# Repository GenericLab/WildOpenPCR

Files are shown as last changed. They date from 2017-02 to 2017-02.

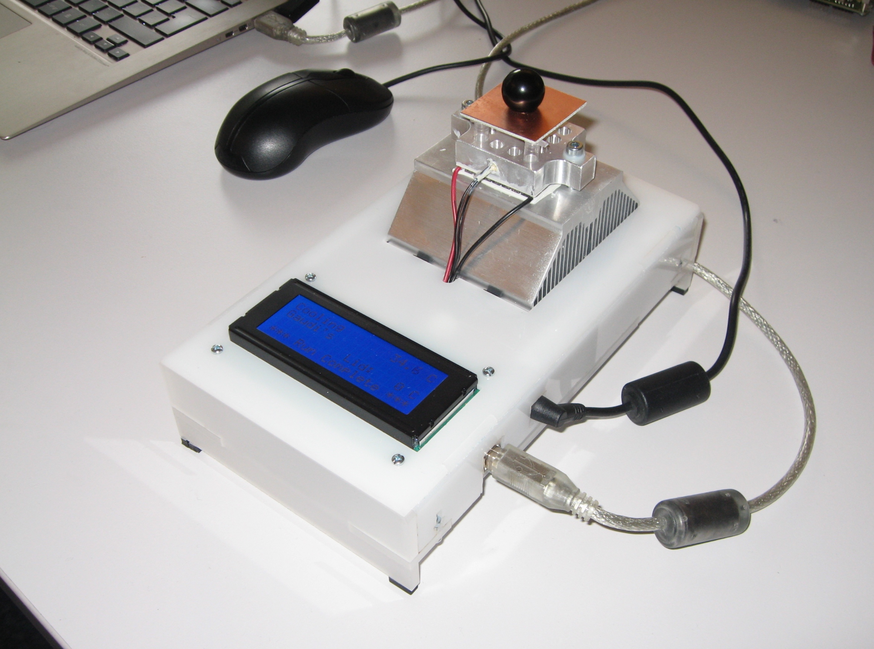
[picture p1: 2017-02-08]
Images/WildOpenPCR.JPG

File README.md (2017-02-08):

# WildOpenPCR
DIY derivate of the OpenPCR Project.
Original design of OpenPCR by Tito Jakowski and Jeff Perfutto: http://openpcr.org/

For more info see: http://wlu18www30.webland.ch/wiki/Wild_OpenPCR

and: http://www.gaudi.ch/GaudiLabs/?page_id=328

All OpenPCR software, design files and instructions are licensed under the GNU GPLv3.

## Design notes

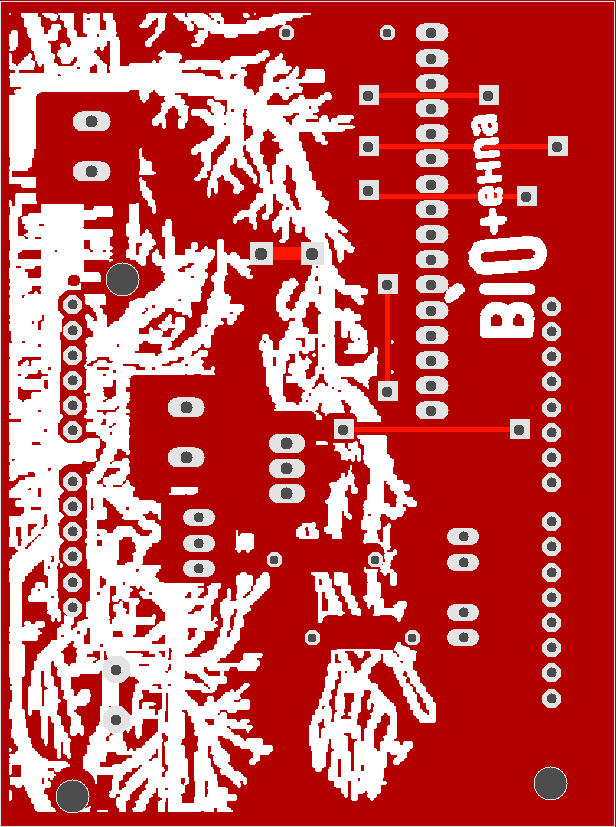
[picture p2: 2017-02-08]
Images/PCRBottom.png

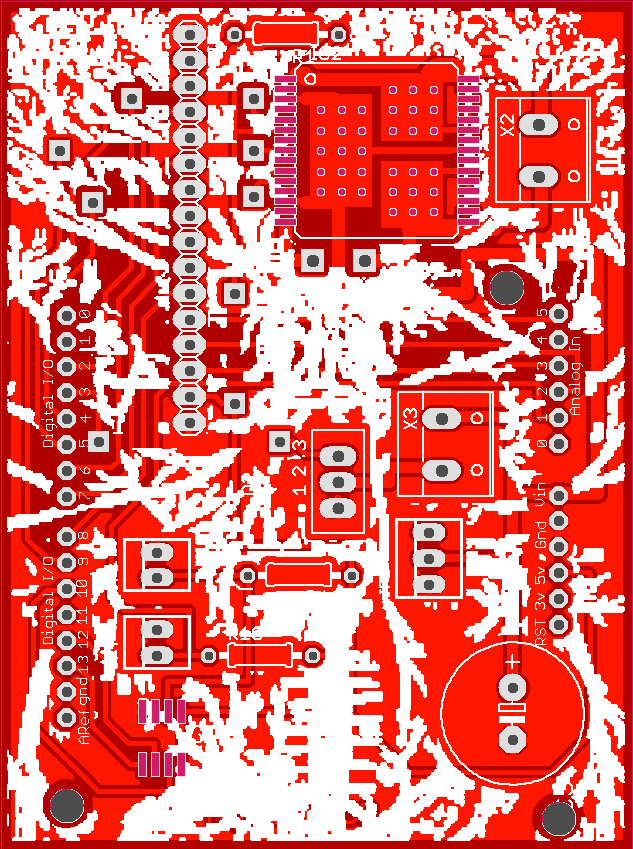
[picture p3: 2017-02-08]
Images/PCRTop.png

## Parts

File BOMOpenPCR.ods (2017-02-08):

 | PART LIST / BILL OF MATERIAL
 | MyOpenPCR
 | Exported |  | from OpenPCRGaudi.b
 | Part | No | Description | Package | Library Position (inc | Price
x | C3 | 1 | 1000 uF, 25V, 5.08 mm RAD 470/35 | E5-13 | rcl (1.975 0.525) |  |  | 5 | 2x 470
x | IC1 | 1 | MCP 3551-E/SN :: A/D Converter / 18-bit / 1-Kanal / 4sps / SO-8 | SO-08 | microchip (0.62 0.43) | 3.7 | 3.7 | 5 | 2
x | IC2 | 1 | VNH 3SP30 :: H-Bridge Motor Driver 30A Power, MSOP-30 | MULTIPOWERSO-30 | Gaudi (1.45 2.7) | 5.5 | 5.5 | 5 | 2
x | JP1 | 1 | 1X16 pinheader MPE 094-1-016 / BL 1X20W 2,54 |  | pinhead (0.725 2.4) |  |  | 5
x | JP2 | 1 | 1x3 pinheader / connector (2.54 mm) SL 1X36G 2,54 | 22-23-2031 | con-molex (1.65 1.125)
x | JP3 | 1 | 1x2 pinheader / connector (2.54 mm) | 22-23-2021 | con-molex (0.6 1.1)
x | JP4 | 1 | 1x2 pinheader / connector (2.54 mm) | 22-23-2021 | con-molex (0.6 0.8)
x | Q2 | 1 | BSS97 / IRFI 540N | TO202 | openpcr (1.1 1.42) | 0.8 | 0.8 | 5 | 2
x | R1 | 1 | 68 Ohm / 1W 68 | 0207/10 | resistor (1.1 3.15) |  |  | 10 | 6
x | R4 | 1 | 2.2 kOhm / METALL 2,20K | 0207/10 | resistor (1.15 1.06) |  |  | 20 | 10
x | R10 | 1 | 2.2 kOhm / METALL 2,20K | 0207/10 | resistor (1 0.75)
 | U$3 | 1 | ARDUINO UNO :: Arduino Uno Rev. 3, ATmega328, USB | ARDUINO | openpcr (2.25 -0.45) | 18.5 | 18.5 | 3 |  | ricardo
x | X2 | 1 | RND 205-00232 1x2 Connetor (5.08 mm) | W237-132 | con-wago-508 (2.1 2.7) |  |  | 10 | 4
x | X3 | 1 | RND 205-00232 1x2 Connetor (5.08 mm) | W237-132 | con-wago-508 (1.725 1.565)
x | NTC | 2 | HYG NTC 103 :: Präzisions-Temperatursensor TS-NTC-103 |  |  | 2.2 | 4.4 | 5 | 3x 1x ohne A
x | LCD | 1 | LCD 204B BL :: LCD Dot-Matrix-Modul, 4x20 Zeichen, blau |  |  | 20 | 20 | 3 | 1
x | PELTIER | 1 | TECB 1 :: Thermo-Modul, Peltierelement, 40x40x3,8mm | 51.4W |  | 19.4 | 19.4 | 3 | 2
 | PELTIER |  | TECB 3 :: Thermo-Modul, Peltierelement, 40x40x3,3mm | 68.6W |  |  |  | 3 | 2
x | MyOpenPCR_PCB
x | TOP_HEATER PCB |  | LidHeater.brd
x | PCB Cooler
 | HEAT_BLOCK
x | POWER SUPPLY | 1 | MW GST90A12 :: Tischnetzteil 80 W, 12 V / 6,67 A |  |  | 28.6 | 28.6
 | Cables (Flat) Jumper |  |  |  |  |  |  |  |  | Ricardo /
 |  |  |  |  |  |  | 100.9
 | PCB Corrections |  | Dickere Brücken
 |  |  | Pin Durchmesser Chechen
 |  |  | Power Anschluss (Pads +/-)
 | Laser: |  | IRLR 120N

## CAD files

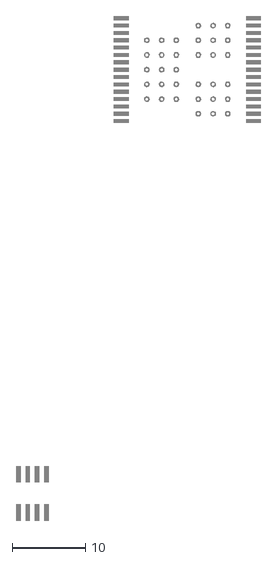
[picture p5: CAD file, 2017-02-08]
MyOpenPCR/OpenPCRGaudi.dxf
33.3 x 68.6

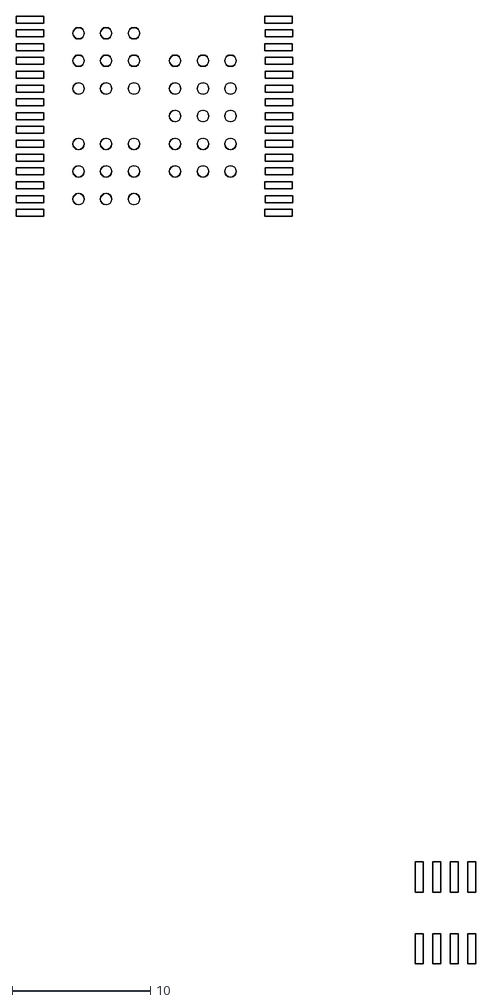
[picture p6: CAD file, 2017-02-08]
Stencils/OpenPCR_Stencil.dxf
33.3 x 68.6

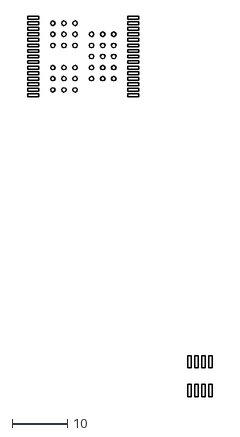
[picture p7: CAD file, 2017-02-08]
Stencils/OpenPCR_Stencil2.dxf
33.3 x 68.6

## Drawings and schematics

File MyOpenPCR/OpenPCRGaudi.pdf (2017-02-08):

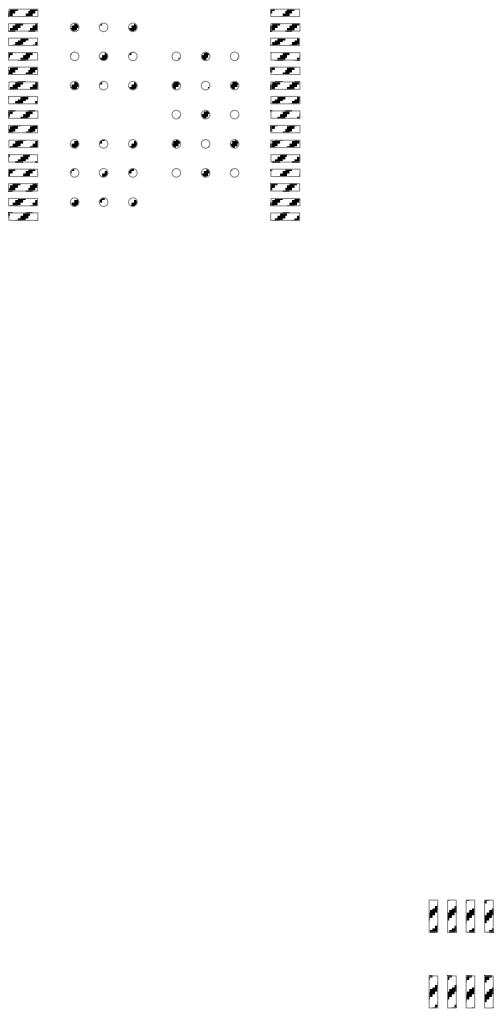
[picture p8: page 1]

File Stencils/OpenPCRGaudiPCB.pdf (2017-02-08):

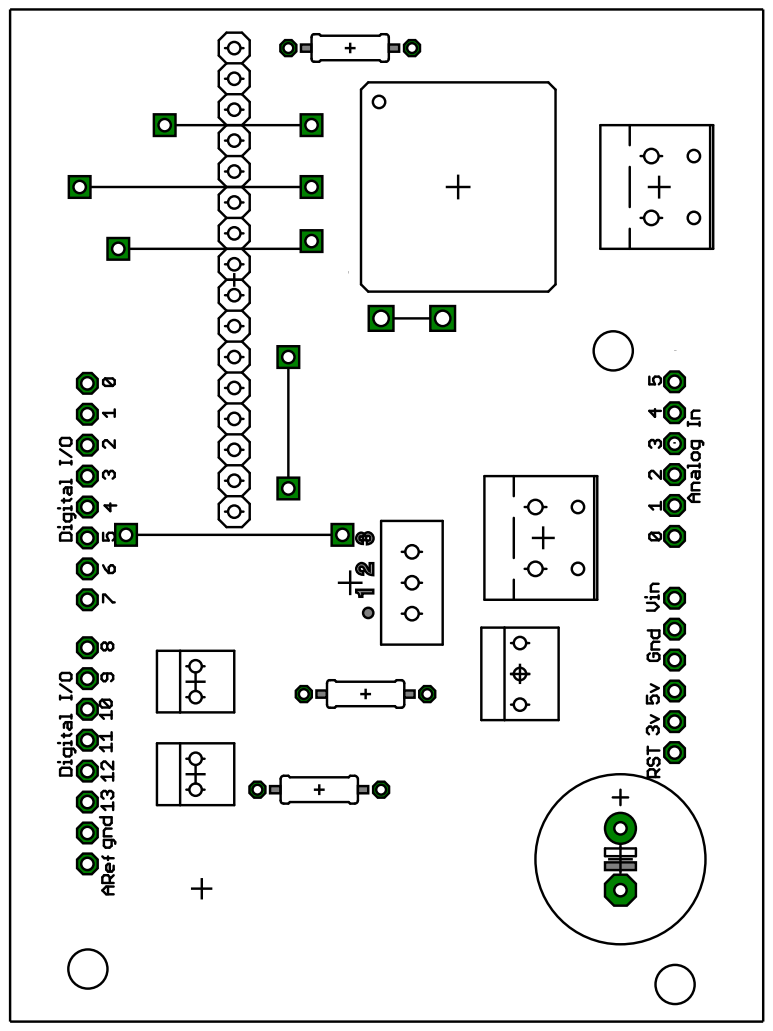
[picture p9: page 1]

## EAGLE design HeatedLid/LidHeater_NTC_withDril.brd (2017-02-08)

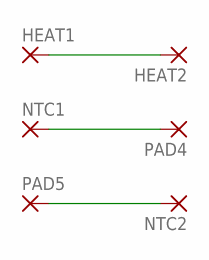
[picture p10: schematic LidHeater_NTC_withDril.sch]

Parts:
HEAT1, HEAT2: SMD5; SMD2,54-5,08
NTC1, NTC2: SMD5; SMD2,54-5,08
PAD4, PAD5: SMD5; SMD2,54-5,08

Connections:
unnamed: HEAT1.1, HEAT2.1
unnamed: NTC1.1, PAD4.1
unnamed: NTC2.1, PAD5.1

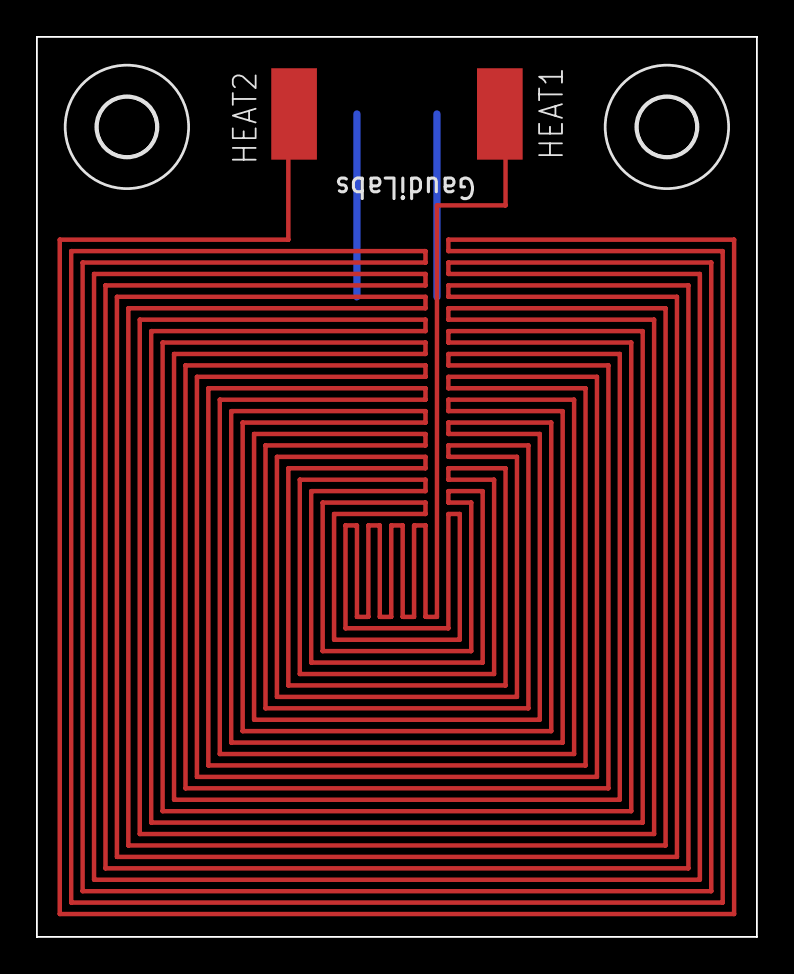
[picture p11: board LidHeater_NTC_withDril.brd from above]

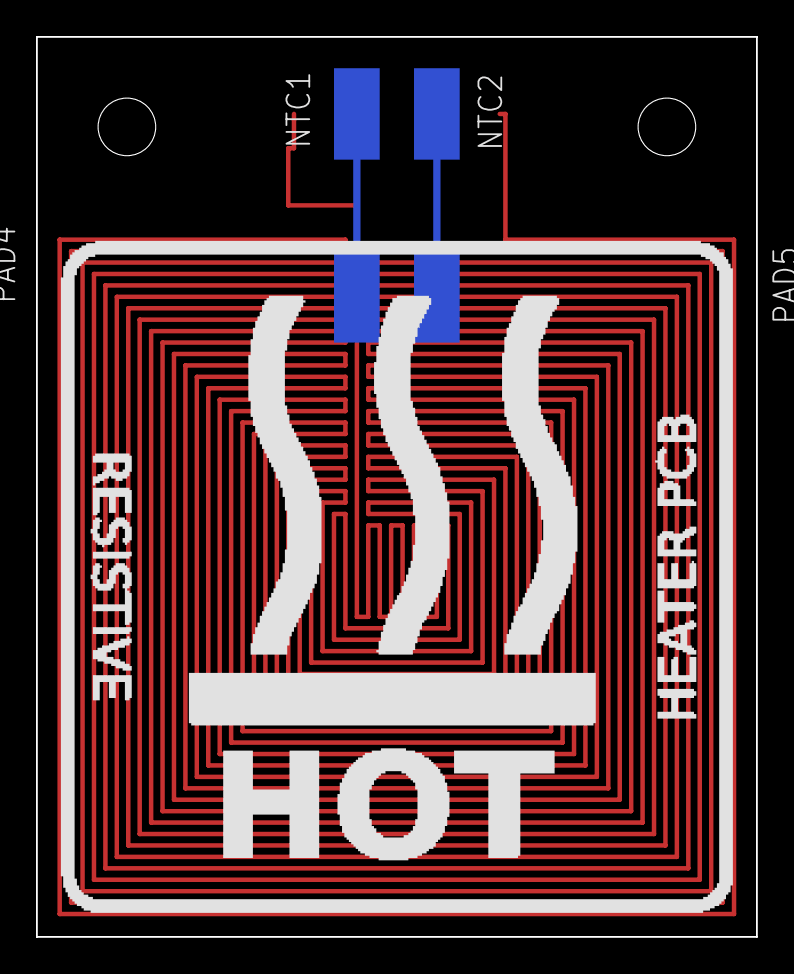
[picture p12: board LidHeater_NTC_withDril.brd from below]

Board: 2 copper layers, 40.0 x 50.0 mm, 8 parts (4 on the bottom side), 3 nets.

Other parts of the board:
U$1, U$2: 3,2

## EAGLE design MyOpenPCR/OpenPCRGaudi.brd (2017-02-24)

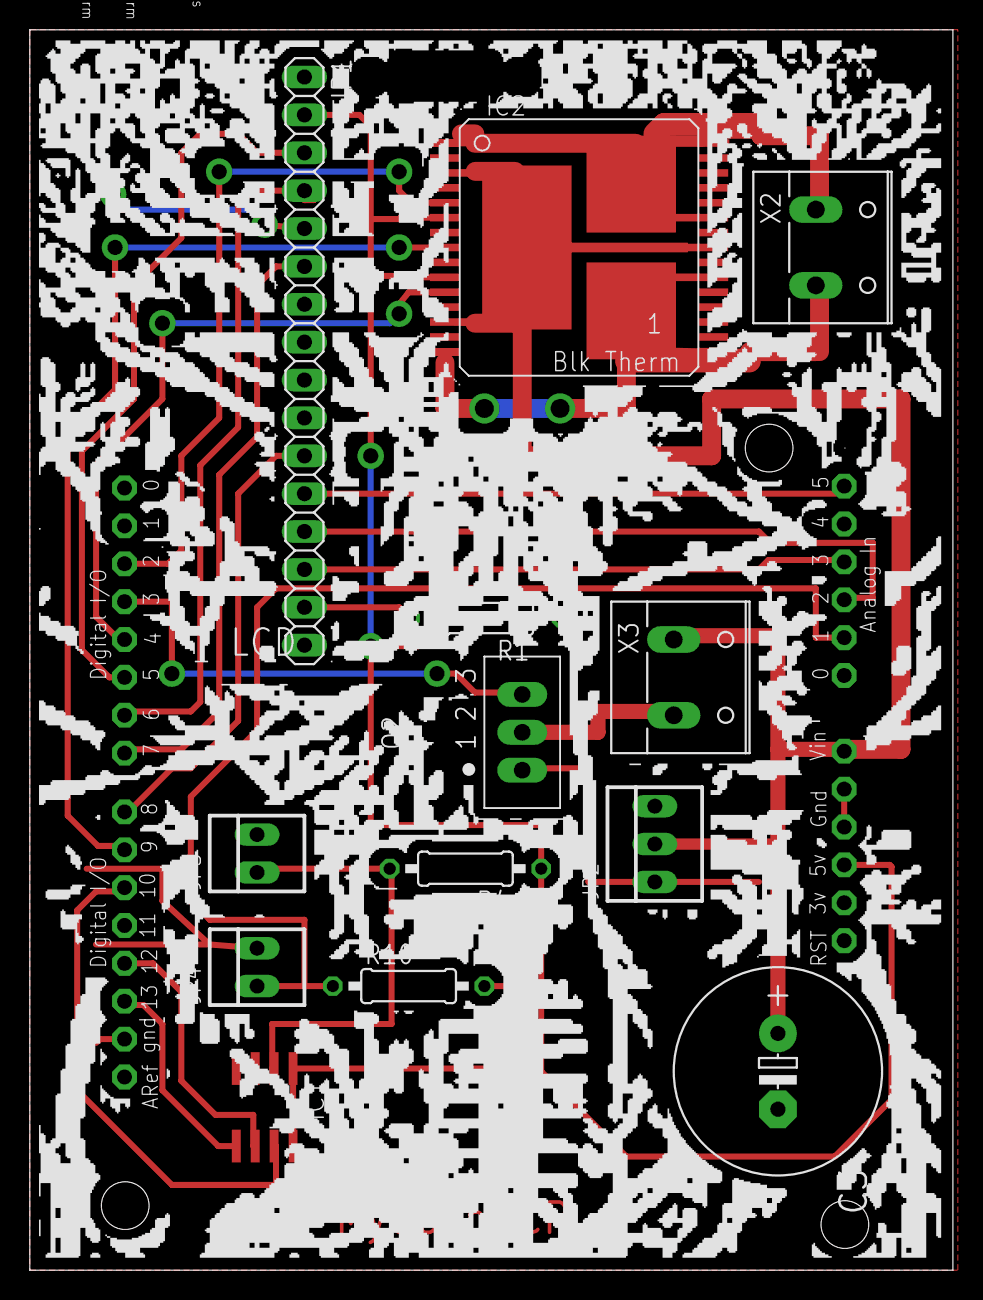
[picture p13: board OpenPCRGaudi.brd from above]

Board: 2 copper layers, 61.9 x 83.2 mm, 14 parts (0 on the bottom side), 23 nets.

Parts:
C3: E5-13
IC1: MCP3551SN; SO-08
IC2: VNH3SP30_2; MULTIPOWERSO-30
JP1: 1X16
JP2: 22-23-2031
JP3, JP4: 22-23-2021
Q2: BSS97; TO202
R1, R4, R10: 0207/10
U$3: ARDUINODUEMILANOVE; ARDUINO
X2, X3: W237-132

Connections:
+5VREG: IC1.1, IC1.8, IC2.6, IC2.10, JP1.2, R1.1, R4.1, R10.2, U$3.5V
+12V1: C3.+, IC2.3, IC2.13, IC2.23, IC2.VCC, IC2.VCC@1, JP2.2, U$3.VIN, X3.1
GND1: C3.-, IC1.3, IC1.4, IC2.18, IC2.19, IC2.20, IC2.26, IC2.27, IC2.28, JP1.1, JP1.5, JP1.16, JP2.1, JP3.2, JP4.2, Q2.1, U$3.GND, U$3.GND1, U$3.GND2
unnamed: JP1.3, U$3.D5
unnamed: JP1.4, U$3.D6
unnamed: JP1.14, U$3.A3
unnamed: JP1.15, R1.2
unnamed: Q2.3, U$3.D3
unnamed: JP1.13, U$3.A2
unnamed: JP1.6, U$3.D7
unnamed: JP1.12, U$3.A5
unnamed: IC1.5, U$3.D13
unnamed: Q2.2, X3.2
unnamed: JP1.11, U$3.D8
unnamed: IC1.2, JP3.1, R4.2
unnamed: IC2.1, IC2.25, IC2.30, IC2.GND, IC2.OUTA, X2.1
unnamed: IC1.6, U$3.D12
unnamed: IC1.7, U$3.D10
unnamed: IC2.8, U$3.D9
unnamed: IC2.11, U$3.D4
unnamed: IC2.15, IC2.16, IC2.21, IC2.OUTB, IC2.SS, X2.2
unnamed: IC2.5, U$3.D2
unnamed: JP4.1, R10.1, U$3.A1

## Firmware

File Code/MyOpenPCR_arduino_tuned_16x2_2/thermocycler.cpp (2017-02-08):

/*
 *  thermocycler.cpp - OpenPCR control software.
 *  Copyright (C) 2010-2012 Josh Perfetto. All Rights Reserved.
 *
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
 *  You should have received a copy of the GNU General Public License along with
 *  the OpenPCR control software.  If not, see <http://www.gnu.org/licenses/>.
 */

#include "pcr_includes.h"
#include "thermocycler.h"

#include "display.h"
#include "program.h"
#include "serialcontrol.h"
#include "../Wire/Wire.h"
#include <avr/pgmspace.h>

//constants
  
// I2C address for MCP3422 - base address for MCP3424
#define MCP3422_ADDRESS 0X68
#define MCP342X_RES_FIELD  0X0C // resolution/rate field
#define MCP342X_18_BIT     0X0C // 18-bit 3.75 SPS
#define MCP342X_BUSY       0X80 // read: output not ready

#define CYCLE_START_TOLERANCE 0.2
#define LID_START_TOLERANCE 1.0

#define PLATE_PID_INC_NORM_P 3000
#define PLATE_PID_INC_NORM_I 750
#define PLATE_PID_INC_NORM_D 3000

#define PLATE_PID_INC_LOW_THRESHOLD 40
#define PLATE_PID_INC_LOW_P 600
#define PLATE_PID_INC_LOW_I 200
#define PLATE_PID_INC_LOW_D 400

#define PLATE_PID_DEC_HIGH_THRESHOLD 70
#define PLATE_PID_DEC_HIGH_P 800
#define PLATE_PID_DEC_HIGH_I 700
#define PLATE_PID_DEC_HIGH_D 300

#define PLATE_PID_DEC_NORM_P 3000
#define PLATE_PID_DEC_NORM_I 750
#define PLATE_PID_DEC_NORM_D 3000

#define PLATE_PID_DEC_LOW_THRESHOLD 35
#define PLATE_PID_DEC_LOW_P 2000
#define PLATE_PID_DEC_LOW_I 100
#define PLATE_PID_DEC_LOW_D 200

#define PLATE_BANGBANG_THRESHOLD 2.0

#define MIN_PELTIER_PWM -1023
#define MAX_PELTIER_PWM 1023

#define MAX_LID_PWM 255
#define MIN_LID_PWM 0

#define STARTUP_DELAY 4000

//pid parameters
const SPIDTuning LID_PID_GAIN_SCHEDULE[] = {
  //maxTemp, kP, kI, kD
  { 70, 40, 0.15, 60 },
  { 200, 80, 1.1, 10 }
};

//public
Thermocycler::Thermocycler(boolean restarted):
  iRestarted(restarted),
  ipDisplay(NULL),
  ipProgram(NULL),
  ipDisplayCycle(NULL),
  ipSerialControl(NULL),
  iProgramState(EStartup),
  ipPreviousStep(NULL),
  ipCurrentStep(NULL),
  iThermalDirection(OFF),
  iPeltierPwm(0),
  iCycleStartTime(0),
  iRamping(true),
  iPlatePid(&iPlateThermistor.GetTemp(), &iPeltierPwm, &iTargetPlateTemp, PLATE_PID_INC_NORM_P, PLATE_PID_INC_NORM_I, PLATE_PID_INC_NORM_D, DIRECT),
  iLidPid(LID_PID_GAIN_SCHEDULE, MIN_LID_PWM, MAX_LID_PWM),
  iTargetLidTemp(0) {
    
  ipDisplay = new Display();
  ipSerialControl = new SerialControl(ipDisplay);
  
  //init pins
  pinMode(15, INPUT);
  pinMode(2, OUTPUT);
  pinMode(3, OUTPUT);
  pinMode(4, OUTPUT);
  pinMode(5, OUTPUT);
  
    // SPCR = 01010000
  //interrupt disabled,spi enabled,msb 1st,master,clk low when idle,
  //sample on leading edge of clk,system clock/4 rate (fastest)
  int clr;
  SPCR = (1<<SPE)|(1<<MSTR)|(1<<4);
  clr=SPSR;
  clr=SPDR;
  delay(10); 

  iPlatePid.SetOutputLimits(MIN_PELTIER_PWM, MAX_PELTIER_PWM);
  
  // Peltier PWM
  TCCR1A |= (1<<WGM11) | (1<<WGM10);
  TCCR1B = _BV(CS21);
  
  // Lid PWM
  TCCR2A = _BV(COM2A1) | _BV(COM2B1) | _BV(WGM21) | _BV(WGM20);
  TCCR2B = _BV(CS22);

  iszProgName[0] = '\0';
}

Thermocycler::~Thermocycler() {
  delete ipSerialControl;
  delete ipDisplay;
}

// accessors
int Thermocycler::GetNumCycles() {
  return ipDisplayCycle->GetNumCycles();
}

int Thermocycler::GetCurrentCycleNum() {
  int numCycles = GetNumCycles();
  return ipDisplayCycle->GetCurrentCycle() > numCycles ? numCycles : ipDisplayCycle->GetCurrentCycle();
}

Thermocycler::ThermalState Thermocycler::GetThermalState() {
  if (iProgramState == EStartup || iProgramState == EStopped)
    return EIdle;
  
  if (iRamping) {
    if (ipPreviousStep != NULL) {
      return ipCurrentStep->GetTemp() > ipPreviousStep->GetTemp() ? EHeating : ECooling;
    } else {
      return iThermalDirection == HEAT ? EHeating : ECooling;
    }
  } else {
    return EHolding;
  }
}
 
// control
void Thermocycler::SetProgram(Cycle* pProgram, Cycle* pDisplayCycle, const char* szProgName, int lidTemp) {
  Stop();

  ipProgram = pProgram;
  ipDisplayCycle = pDisplayCycle;

  strcpy(iszProgName, szProgName);
  iTargetLidTemp = lidTemp;
}

void Thermocycler::Stop() {
  iProgramState = EStopped;
  
  ipProgram = NULL;
  ipPreviousStep = NULL;
  ipCurrentStep = NULL;
  
  iStepPool.ResetPool();
  iCyclePool.ResetPool();
  
  ipDisplay->Clear();
}

PcrStatus Thermocycler::Start() {
  if (ipProgram == NULL)
    return ENoProgram;
  
  //advance to lid wait state
  iProgramState = ELidWait;
  
  return ESuccess;
}
    
// internal
void Thermocycler::Loop() {
  switch (iProgramState) {
  case EStartup:
    if (millis() > STARTUP_DELAY) {
      iProgramState = EStopped;
      
      if (!iRestarted && !ipSerialControl->CommandReceived()) {
        //check for stored program
        SCommand command;
        if (ProgramStore::RetrieveProgram(command, (char*)ipSerialControl->GetBuffer()))
          ProcessCommand(command);
      }
    }
    break;

  case ELidWait:    
    if (GetLidTemp() >= iTargetLidTemp - LID_START_TOLERANCE) {
      //lid has warmed, begin program
      iThermalDirection = OFF;
      iPeltierPwm = 0;
      PreprocessProgram();
      iProgramState = ERunning;
      
      ipProgram->BeginIteration();
      AdvanceToNextStep();
      
      iProgramStartTimeMs = millis();
    }
    break;
  
  case ERunning:
    //update program
    if (iProgramState == ERunning) {
      if (iRamping && abs(ipCurrentStep->GetTemp() - GetPlateTemp()) <= CYCLE_START_TOLERANCE && GetRampElapsedTimeMs() > ipCurrentStep->GetRampDurationS() * 1000) {
        //begin step hold
        
        //eta updates
        if (ipCurrentStep->GetRampDurationS() == 0) {
          //fast ramp
          iElapsedFastRampDegrees += absf(GetPlateTemp() - iRampStartTemp);
          iTotalElapsedFastRampDurationMs += millis() - iRampStartTime;
        }
        
        if (iRampStartTemp > GetPlateTemp())
          iHasCooled = true;
        iRamping = false;
        iCycleStartTime = millis();
        
      } else if (!iRamping && !ipCurrentStep->IsFinal() && millis() - iCycleStartTime > (unsigned long)ipCurrentStep->GetStepDurationS() * 1000) {
        //begin next step
        AdvanceToNextStep();
          
        //check for program completion
        if (ipCurrentStep == NULL || ipCurrentStep->IsFinal())
          iProgramState = EComplete;        
      }
    }
    break;
    
  case EComplete:
    if (iRamping && ipCurrentStep != NULL && abs(ipCurrentStep->GetTemp() - GetPlateTemp()) <= CYCLE_START_TOLERANCE)
      iRamping = false;
    break;
  }
  
  //lid 
  iLidThermistor.ReadTemp();
  ControlLid();
  
  //plate  
  iPlateThermistor.ReadTemp();
  CalcPlateTarget();
  ControlPeltier();
  
  //program
  UpdateEta();
  ipDisplay->Update();
  ipSerialControl->Process();
}

//private
void Thermocycler::AdvanceToNextStep() {
  ipPreviousStep = ipCurrentStep;
  ipCurrentStep = ipProgram->GetNextStep();
  if (ipCurrentStep == NULL)
    return;
  
  //update eta calc params
  if (ipPreviousStep == NULL || ipPreviousStep->GetTemp() != ipCurrentStep->GetTemp()) {
    iRamping = true;
    iRampStartTime = millis();
    iRampStartTemp = GetPlateTemp();
  } else {
    iCycleStartTime = millis(); //next step starts immediately
  }
  
  CalcPlateTarget();
  SetPlateControlStrategy();
}

void Thermocycler::SetPlateControlStrategy() {
  if (InControlledRamp())
    return;
    
  if (absf(iTargetPlateTemp - GetPlateTemp()) >= PLATE_BANGBANG_THRESHOLD && !InControlledRamp()) {
    iPlateControlMode = EBangBang;
    iPlatePid.SetMode(MANUAL);
  } else {
    iPlateControlMode = EPIDPlate;
    iPlatePid.SetMode(AUTOMATIC);
  }
  
  if (iRamping) {
    if (iTargetPlateTemp >= GetPlateTemp()) {
      iDecreasing = false;
      if (iTargetPlateTemp < PLATE_PID_INC_LOW_THRESHOLD)
        iPlatePid.SetTunings(PLATE_PID_INC_LOW_P, PLATE_PID_INC_LOW_I, PLATE_PID_INC_LOW_D);
      else
        iPlatePid.SetTunings(PLATE_PID_INC_NORM_P, PLATE_PID_INC_NORM_I, PLATE_PID_INC_NORM_D);

    } else {
      iDecreasing = true;
      if (iTargetPlateTemp > PLATE_PID_DEC_HIGH_THRESHOLD)
        iPlatePid.SetTunings(PLATE_PID_DEC_HIGH_P, PLATE_PID_DEC_HIGH_I, PLATE_PID_DEC_HIGH_D);
      else if (iTargetPlateTemp < PLATE_PID_DEC_LOW_THRESHOLD)
        iPlatePid.SetTunings(PLATE_PID_DEC_LOW_P, PLATE_PID_DEC_LOW_I, PLATE_PID_DEC_LOW_D);
      else
        iPlatePid.SetTunings(PLATE_PID_DEC_NORM_P, PLATE_PID_DEC_NORM_I, PLATE_PID_DEC_NORM_D);
    }
  }
}

void Thermocycler::CalcPlateTarget() {
  if (ipCurrentStep == NULL)
    return;
  
  if (InControlledRamp()) {
    //controlled ramp
    double tempDelta = ipCurrentStep->GetTemp() - ipPreviousStep->GetTemp();
    double rampPoint = (double)GetRampElapsedTimeMs() / (ipCurrentStep->GetRampDurationS() * 1000);
    iTargetPlateTemp = ipPreviousStep->GetTemp() + tempDelta * rampPoint;
    
  } else {
    //fast ramp
    iTargetPlateTemp = ipCurrentStep->GetTemp();
  }
}

void Thermocycler::ControlPeltier() {
  ThermalDirection newDirection = OFF;
  
  if (iProgramState == ERunning || (iProgramState == EComplete && ipCurrentStep != NULL)) {
    // Check whether we are nearing target and should switch to PID control
    if (iPlateControlMode == EBangBang && absf(iTargetPlateTemp - GetPlateTemp()) < PLATE_BANGBANG_THRESHOLD) {
      iPlateControlMode = EPIDPlate;
      iPlatePid.SetMode(AUTOMATIC);
      iPlatePid.ResetI();
    }
 
    // Apply control mode
    if (iPlateControlMode == EBangBang)
      iPeltierPwm = iTargetPlateTemp > GetPlateTemp() ? MAX_PELTIER_PWM : MIN_PELTIER_PWM;
    iPlatePid.Compute();
    
    if (iDecreasing && iTargetPlateTemp > PLATE_PID_DEC_LOW_THRESHOLD) {
      if (iTargetPlateTemp < GetPlateTemp())
        iPlatePid.ResetI();
      else
        iDecreasing = false;
    } 
    
    if (iPeltierPwm > 0)
      newDirection = HEAT;
    else if (iPeltierPwm < 0)
      newDirection = COOL; 
    else
      newDirection = OFF;
  } else {
    iPeltierPwm = 0;
  }
  
  iThermalDirection = newDirection;
  SetPeltier(newDirection, abs(iPeltierPwm));
}

void Thermocycler::ControlLid() {
  int drive = 0;  
  if (iProgramState == ERunning || iProgramState == ELidWait)
    drive = iLidPid.Compute(iTargetLidTemp, GetLidTemp());
 
  analogWrite(3, drive);
}

//PreprocessProgram initializes ETA parameters and validates/modifies ramp conditions
void Thermocycler::PreprocessProgram() {
  Step* pCurrentStep;
  Step* pPreviousStep = NULL;
  
  iProgramHoldDurationS = 0;
  iEstimatedTimeRemainingS = 0;
  iHasCooled = false;
  
  iProgramControlledRampDurationS = 0;
  iProgramFastRampDegrees = 0;
  iElapsedFastRampDegrees = 0;
  iTotalElapsedFastRampDurationMs = 0;  
  
  ipProgram->BeginIteration();
  while ((pCurrentStep = ipProgram->GetNextStep()) && !pCurrentStep->IsFinal()) {
    //validate ramp
    if (pPreviousStep != NULL && pCurrentStep->GetRampDurationS() * 1000 < absf(pCurrentStep->GetTemp() - pPreviousStep->GetTemp()) * PLATE_FAST_RAMP_THRESHOLD_MS) {
      //cannot ramp that fast, ignored set ramp
      pCurrentStep->SetRampDurationS(0);
    }
    
    //update eta hold
    iProgramHoldDurationS += pCurrentStep->GetStepDurationS();
 
    //update eta ramp
    if (pCurrentStep->GetRampDurationS() > 0) {
      //controlled ramp
      iProgramControlledRampDurationS += pCurrentStep->GetRampDurationS();
    } else {
      //fast ramp
      double previousTemp = pPreviousStep ? pPreviousStep->GetTemp() : GetPlateTemp();
      iProgramFastRampDegrees += absf(previousTemp - pCurrentStep->GetTemp()) - CYCLE_START_TOLERANCE;
    }
    
    pPreviousStep = pCurrentStep;
  }
}
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

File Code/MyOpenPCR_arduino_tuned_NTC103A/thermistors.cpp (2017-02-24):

/*
 *  program.cpp - OpenPCR control software.
 *  Copyright (C) 2010-2012 Josh Perfetto. All Rights Reserved.
 *
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
 *  You should have received a copy of the GNU General Public License along with
 *  the OpenPCR control software.  If not, see <http://www.gnu.org/licenses/>.
 */

#include "pcr_includes.h"
#include "thermistors.h"

// lid resistance table, in Ohms
PROGMEM const unsigned int LID_RESISTANCE_TABLE[] = {  
33890,32138,30487,28933,27468,26088,24785,23557,22397,21302,
20268,19291,18367,17493,16667,15885,15145,14444,13780,13151
12554,11988,11452,10942,10459,10000,9564,9150,8756,8382
8026,7687,7365,7058,6765,6487,6222,5969,5728,5499
5279,5070,4871,4680,4498,4324,4158,4000,3848,3703
3564,3431,3304,3183,3066,2955,2848,2746,2648,2554
2463,2377,2294,2215,2138,2065,1995,1927,1862,1800
1740,1682,1627,1574,1522,1473,1426,1380,1336,1294
1253,1214,1176,1140,1105,1071,1038,1007,977,947
919,892,866,840,816,792,769,747,726,705
685,666,648,630,612,595,579,563,548,533
519,505,492,479,466,454,442,431,420,409
399,389,379,369,360,351





};

// plate resistance table, in 0.1 Ohms
PROGMEM const unsigned long PLATE_RESISTANCE_TABLE[] = {
411749,382827,356157,331548,308825,287832,268423,250469,233850,218457
204192,190964,178691,167297,156712,146875,137727,129215,121291,113910
107031,100617,94633,89048,83831,78958,74402,70141,66154,62421
58925,55649,52578,49698,46995,44458,42075,39836,37731,35752
33890,32138,30487,28933,27468,26088,24785,23557,22397,21302
20268,19291,18367,17493,16667,15885,15145,14444,13780,13151
12554,11988,11452,10942,10459,10000,9564,9150,8756,8382
8026,7687,7365,7058,6765,6487,6222,5969,5728,5499
5279,5070,4871,4680,4498,4324,4158,4000,3848,3703
3564,3431,3304,3183,3066,2955,2848,2746,2648,2554
2463,2377,2294,2215,2138,2065,1995,1927,1862,1800
1740,1682,1627,1574,1522,1473,1426,1380,1336,1294
1253,1214,1176,1140,1105,1071,1038,1007,977,947
919,892,866,840,816,792,769,747,726,705
685,666,648,630,612,595

};
  
//spi
#define DATAOUT 11//MOSI
#define DATAIN  12//MISO 
#define SPICLOCK  13//sck
#define SLAVESELECT 10//ss

//------------------------------------------------------------------------------
float TableLookup(const unsigned long lookupTable[], unsigned int tableSize, int startValue, unsigned long searchValue) {
  //simple linear search for now
  int i;
  for (i = 0; i < tableSize; i++) {
    if (searchValue >= pgm_read_dword_near(lookupTable + i))
      break;
  }
  
  if (i > 0) {
    unsigned long high_val = pgm_read_dword_near(lookupTable + i - 1);
    unsigned long low_val = pgm_read_dword_near(lookupTable + i);
    return i + startValue - (float)(searchValue - low_val) / (float)(high_val - low_val);
  } else {
    return startValue;
  }
}
//------------------------------------------------------------------------------
float TableLookup(const unsigned int lookupTable[], unsigned int tableSize, int startValue, unsigned long searchValue) {
  //simple linear search for now
  int i;
  for (i = 0; i < tableSize; i++) {
    if (searchValue >= pgm_read_word_near(lookupTable + i))
      break;
  }
  
  if (i > 0) {
    unsigned long high_val = pgm_read_word_near(lookupTable + i - 1);
    unsigned long low_val = pgm_read_word_near(lookupTable + i);
    return i + startValue - (float)(searchValue - low_val) / (float)(high_val - low_val);
  } else {
    return startValue;
  }
}
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

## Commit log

2017-02-08 first upload wildOpenPCR
    [BOMOpenPCR.ods, LidHeater_NTC.GBL, LidHeater_NTC.GBO, LidHeater_NTC.GBP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]
2017-02-24 fixed an error on the PCB and added new Code
    for two line LCD and different temp sensor.
    [OpenPCRGaudi.brd]

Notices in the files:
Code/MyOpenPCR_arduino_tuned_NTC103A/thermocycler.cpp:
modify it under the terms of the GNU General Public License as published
